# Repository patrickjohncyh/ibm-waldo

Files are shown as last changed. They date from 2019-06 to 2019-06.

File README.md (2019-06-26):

WALDO
======

Introduction
------------

People with learning disabilities can encounter difficulty in expressing themselves in speech. Makaton is a language programme that uses signs and symbols to enable users of all ages to communicate effectively. WALDO is a machine learning-enabled assisted living device meant for use by Makaton users and their carers in a care home setting. WALDO’s capabilities include:

* Makaton sign language interpretation using machine learning
* Easy-to-use interface, and a cute and endearing package to encourage use by people with learning disabilities and their carers
* Programmable buttons for users to quickly express pre-set phrases or emotions

Intended Use
---

WALDO is intended for use in a care home setting in the following ways:

Makaton sign interpretation
1. Makaton user (care home patient) signs to WALDO
2. WALDO uses machine learning to interpret sign
3. WALDO vocalises sign for carer to understand what user intends to express
4. Carer reacts accordingly, completing the interaction between the user and carer
This implementation enables the carer to understand the user without having to undergo the time-consuming process of learning Makaton.

Expression of pre-set phrases/emotions
1. User (by him/herself, or via carer) sets common phrases that he/she uses frequently to correspond to physical buttons on WALDO
2. User labels buttons accordingly for ease of use
3. User presses the relevant button, WALDO vocalises pre-set phrase
4. Carer responds accordingly
This implementation enables people with learning disabilities that have difficulty expressing themselves in speech to easily express everyday sentiments.

Virtual Design History File Overview
---

This is an overview of the various sections and subsections of WALDO's Virtual Design History File (VDHF). The VDHF details the developmental process of WALDO, the necessary steps to recreate it and the ethical and sustainability considerations of WALDO.

<table>
  <tr>
    <th width="18%">Section</th>
    <th width="22%">Subsection</th>
    <th>Description</th>
  </tr>
  <tr>
    <td colspan="2"><span style="font-weight:bold">Overview</span></td>
    <td>Overview of WALDO, contents of Virtual Design History File</td>
  </tr>
  <tr>
    <td rowspan="3"><span style="font-weight:bold">1. Setup</span></td>
    <td> <a href="https://github.com/patrickjohncyh/ibm-waldo/blob/master/1-Setup/1-1-Jetson-Setup.md">1.1 Jetson Nano Setup</a></td>
    <td>Jetson Nano Setup Guide</td>
  </tr>
  <tr>
    <td><a href="https://github.com/patrickjohncyh/ibm-waldo/blob/master/1-Setup/1-2-Pi-Setup.md">1.2 Pi Setup</a></td>
    <td>Raspberry Pi Setup Guide</td>
  </tr>
  <tr>
    <td><a href="https://github.com/patrickjohncyh/ibm-waldo/blob/master/1-Setup/1-3-Hardware-Connections.md">1.3 Hardware Setup</a></td>
    <td>Diagram of device hardware connections</td>
  </tr>
  <tr>
    <td rowspan="5"><span style="font-weight:bold">2. Machine Learning</span></td>
    <td><a href="https://github.com/patrickjohncyh/ibm-waldo/blob/master/2-MachineLearning/2-1-Machine-Learning.md"> 2.1 Machine Learning </a></td>
    <td>Details model design history and evolution as well as implementation on the edge device</td>
  </tr>
  <tr>
    <td><a href="https://github.com/patrickjohncyh/ibm-waldo/blob/master/2-MachineLearning/2-2-Server-Environment-Setup.md"> 2.2 Server Environment Setup</a></td>
    <td>Setting up server environment for further model training</td>
  </tr>
  <tr>
    <td><a href="https://github.com/patrickjohncyh/ibm-waldo/tree/master/2-MachineLearning/server-training"> Server Training Code</a></td>
    <td>Code to be run on server for model training</td>
  </tr>
  <tr>
    <td><a href ="https://github.com/patrickjohncyh/ibm-waldo/tree/master/2-MachineLearning/jetson-execution">Jetson Nano Execution Code</a></td>
    <td>Code to be run on Jetson Nano for Makaton sign recognition</td>
  </tr>
  <tr>
    <td><a href = "https://github.com/patrickjohncyh/ibm-waldo/tree/master/2-MachineLearning/jetson-execution/checkpoint_models"> Model and Weights</a></td>
    <td>Saved weights of the final trained model</td>
  </tr>

  <tr>
    <td rowspan="4"><span style="font-weight:bold">3. Raspberry Pi</span></td>
    <td><a href="https://github.com/patrickjohncyh/ibm-waldo/blob/master/3-Pi/3-1-Pi-Function.md"> 3.1 Overview of Pi Function</a></td>
    <td>Outline of functions and connections of Pi</td>
  </tr>
  <tr>
    <td><a href="https://github.com/patrickjohncyh/ibm-waldo/tree/master/3-Pi/pi-execution"> Pi Execution Code</td>
    <td>Code to be run on Raspberry Pi for high level tasks and audio generations through the IBM Watson text to speech module</span></td>
  </tr>
  <tr>
    
  </tr>
  <tr>
    
  </tr>
  <tr>
    <td rowspan="3"><span style="font-weight:bold">4. Hardware</span></td>
    <td><a href="https://github.com/patrickjohncyh/ibm-waldo/tree/master/4-Hardware/4-1-3D-Printing-STL-Files">4.1 3D printing files</a></td>
    <td>Contains Standard Tessellation Language (STL) files of the Jetson Nano case, the Pi case, the button support structure and WALDO’s eyepiece</td>
  </tr>
  <tr>
    <td><a href="https://github.com/patrickjohncyh/ibm-waldo/blob/master/4-Hardware/4-2-Power-Supply.md">4.2 Power Supply</td>
    <td>Summary of considerations when choosing WALDO’s power supply</td>
  </tr>
  <tr>
    <td><a href="https://github.com/patrickjohncyh/ibm-waldo/blob/master/4-Hardware/4-3-Hardware-List.md">4.3 Hardware List</td>
    <td>List of all hardware components used in assembly of WALDO</td>
  </tr>
  <tr>
    <td rowspan="4"><span style="font-weight:bold">5. Administrative</span></td>
    <td><a href="https://github.com/patrickjohncyh/ibm-waldo/tree/master/5-Administrative/5-1-Record-of-Meetings">5.1 Record of Meetings</td>
    <td>Meeting minutes and decisions made</td>
  </tr>
  <tr>
    <td><a href="https://github.com/patrickjohncyh/ibm-waldo/blob/master/5-Administrative/5-2-Gantt-Chart.md">5.2 Gantt Chart</td>
    <td>Intended timeline of project (plotted during first meeting at IBM Hursley)</td>
  </tr>
  <tr>
    <td><a href="https://github.com/patrickjohncyh/ibm-waldo/blob/master/5-Administrative/5-3-Bill-of-Materials.md">5.3 Bill of Materials</td>
    <td>Record of expenditure and outline of cost of device</td>
  </tr>
  <tr>
    <td><a href="https://github.com/patrickjohncyh/ibm-waldo/blob/master/5-Administrative/5-4-Data-Collection.md">5.4 Data Collection</td>
    <td>Outline of procedure, considerations and product of data collection</td>
  </tr>
  <tr>
    <td rowspan="6"><span style="font-weight:bold">6. Miscellaneous</span></td>
    <td><a href="https://github.com/patrickjohncyh/ibm-waldo/blob/master/6-Miscellaneous/6-1-Ethical-Considerations.md">6.1 Ethical Considerations</td>
    <td>Outline of ethical considerations in the design, building and use of WALDO</td>
  </tr>
  <tr>
    <td><a href="https://github.com/patrickjohncyh/ibm-waldo/blob/master/6-Miscellaneous/6-2-Sustainability-Considerations.md"> 6.2 Sustainability considerations</td>
    <td>Outline of sustainability considerations in the design, building and use of WALDO</td>
  </tr>
  <tr>
    <td><a href="https://github.com/patrickjohncyh/ibm-waldo/blob/master/6-Miscellaneous/6-3-Blog.md">6.3 Blog</td>
    <td>Rationale behind the blog and links to the blog posts</td>
  </tr>
  <tr>
    <td><a href="https://github.com/patrickjohncyh/ibm-waldo/blob/master/6-Miscellaneous/6-4-Future-Work.md">6.4 Future Work</td>
    <td>Discussion of present implementation and possible extensions to the project</td>
  </tr>
  <tr>
    <td><a href="https://github.com/patrickjohncyh/ibm-waldo/blob/master/6-Miscellaneous/6-5-Leaflet.pdf">6.5 Leaflet</td>
    <td>Informational leaflet on WALDO</td>
  </tr>
  <tr>
    <td><a href="https://github.com/patrickjohncyh/ibm-waldo/blob/master/6-Miscellaneous/6-6-Poster.pdf">6.6 Poster</td>
    <td>Poster for hackbooth and presentation</td>
  </tr>
</table>

Acknowledgements
---

The WALDO team consists of 5 students from the Electrical Engineering (EE) Department of Imperial College London. The key tasks performed by each member is as follows,

1. [Joshua Chan](https://github.com/josh8chan) : Administrative, Data Collection, Peripheral Sensors Implementation 
2. [Lua Ying Hao](https://github.com/Kaynelua) : Jetson Nano Implementation, Machine Learning
3. [Ng Yi Song](https://github.com/NgYiSong) : Data Collection, Peripheral Sensors Implementation
4. [Patrick John Chia](https://github.com/patrickjohncyh) : Jetson Nano Implementation, Machine Learning
5. [Yeow En Kai Joel](https://github.com/joelyeow) : Administrative, Data Collection and Processing, Peripheral Sensors Implementation 

We would like to thank:

1. Dr Steve Wright, for his invaluable guidance and encouragement throughout the project
2. Louise Cooper, John McNamara & Emily Larkin from IBM for their clear direction and unwavering support in the implementation of this project
3. Precious Homes, for supporting this project by providing valuable insight into the use of Makaton, as well as training videos
4. Vic, May & Amine at the teaching labs, for their untiring technical support
5. All who volunteered their time to help us in the collection of training data

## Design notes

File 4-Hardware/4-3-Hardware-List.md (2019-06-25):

# 4.3 List of Main Hardware Components

The following table shows the various components bought and used in the assembly of WALDO:

<Br>

| Item                                 	| Product Description                                                                                                                                                                  	| Manufacturer    	| Quantity 	| 
|--------------------------------------	|--------------------------------------------------------------------------------------------------------------------------------------------------------------------------------------	|-----------------	|----------	|
| Elephant Stuffed Toy                 	| Fuddlewuddle Elephant, Medium- H23 cm                                                                                                                                                	| Jellycat        	| 1        	| 
| Jetson Nano                          	| NVIDIA Jetson Nano Developer Kit                                                                                                                                                     	| NVIDIA          	| 1        	| 
| 64GB Micro SD Card for Jetson        	| INMSDX64G10-90U1 - 64GB Ultima Pro Class 10 MicroSDXC Memory Card with SD Adaptor 90MB/s                                                                                             	| Integral        	| 1        	| 
| Cooling Fan for Jetson               	| Noctua NF-A4x20 5V PWM, Premium Quiet Fan, 4-Pin, 5V Version (40x20mm, Brown)                                                                                                        	| Noctua          	| 1        	| 
| Power Adapter for Jetson             	| RS PRO, 20W Plug In,Power Supply 5V, 4A, Level VI Efficiency, 1 Output Switched Mode Power Supply, 3-Pin UK                                                                          	| RS PRO          	| 1        	| 
| Webcam                               	| Logitech C920 HD Pro Webcam                                                                                                                                                          	| Logitech        	| 1        	|
| Wifi Dongle                          	| EW-7811UN - N150 Wi-Fi Nano USB Adaptor                                                                                                                                              	| Edimax          	| 1        	| 
| Power Bank                           	| Krisdonia Laptop Power Bank 25000mAh Portable Charger with Type-C Port + DC Port + Dual USB (QC3.0 Quick Charge) for Laptop, Tablet, Cell phone, Macbook, Camera, Projector and more 	| Krisdonia       	| 1        	| 
| Raspberry Pi                         	| Raspberry Pi 3 Model B                                                                                                                                                               	| Raspberry Pi    	| 1        	| 
| 8GB Micro SD Card for Raspberry Pi   	| Kingston 8GB Micro SDHC Class 4 Memory Card                                                                                                                                          	| Kingston        	| 1        	| 
| Speakers                             	| 00173130 - Sonic Mobil 181 2.0 PC Speakers 3W Black                                                                                                                                  	| Hama            	| 1        	|
| Buttons                              	| 1825910-6: Black Button Tactile Switch, Single Pole Single Throw (SPST) 50 mA @ 24 V dc 1.4mm                                                                                        	| TE Connectivity 	| 4        	| 
| Ultrasonic sensor                    	| Parallax Inc 28015, PING))) Ultrasonic Distance Sensor Module                                                                                                                        	| Parallax Inc    	| 1        	| 
| Hook and Loop Fasteners- Velcro Tape 	| VELCRO Brand Stick On For,Fabrics Tape, 19 mm x 60 cm - White                                                                                                                        	| Velcro Brand    	| 1        	| 

<Br>

> Note that some of the supplementary and commonly found hardware such as jumper cables, wires and the 3D Prints were not included in this list.

<Br>
  
> Also note that this list does not show the cost of each item. The Bill of Materials (which shows the cost of each item) can be found by navigating to "5-Adminisitrative > [5-3-Bill-of-Materials.md](https://github.com/patrickjohncyh/ibm-waldo/blob/master/5-Administrative/5-3-Bill-of-Materials.md)".

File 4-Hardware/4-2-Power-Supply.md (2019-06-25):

# 4.2 Power Source

A strong and stable power supply is needed to power WALDO. In order to choose an appropriate power supply, the power consumption of the individual components of WALDO first needs to be known. This is summarised in the table below. 

| Component                 	| Typical Current Drawn / A 	| Power       Consumption / W 	|
|---------------------------	|:-------------------------:	|:---------------------:	|
| Jetson Nano Developer Kit 	|         1.0 - 2.0         	|       5.0 - 10.0      	|
| Raspberry Pi              	|            0.7            	|          3.5          	|
| Speakers                  	|            0.6            	|          3.0          	|

As such, the power source has to be able to supply about 20W of power to ensure stable and smooth operation. The biggest source of power consumption comes from the Jetson Nano when it is performing its Machine Learning inference task. The most efficient way to power the Jetson Nano would be through the DC barrel jack connector. However, in order to do so, a jumper pin needs to be placed on J48 on the Jetson board, as seen in the diagram below. This enables the Jetson to be powered through the barrel jack.

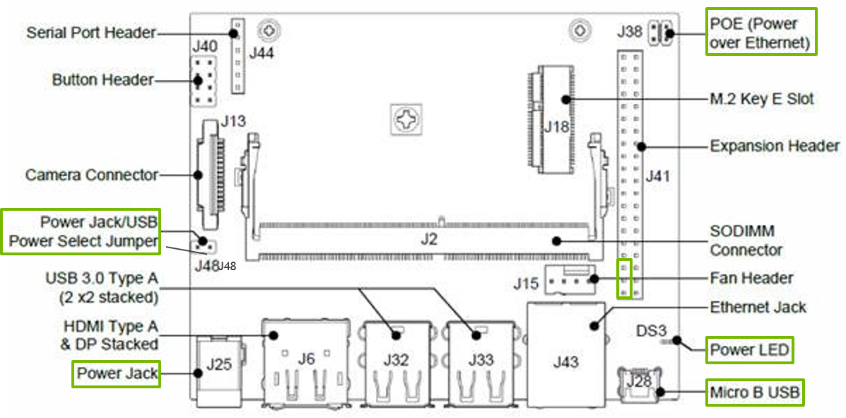
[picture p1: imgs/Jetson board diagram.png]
Jetson Board Layout


One way to power the Jetson would be to use a 4A, 5V plug-in power adapter from the mains. However, this means that WALDO would no longer be portable hence making this option not ideal.

As such, a large power bank was used instead. As a rule of thumb, the power bank chosen should be one capable of charging laptops and should have a DC output port. In this project, the Krisdonia Laptop Power Bank 25000mAh Portable Charger was used. This power bank has a DC output port and 2 USB ports, which fits in nicely for the number of components that require power. The Jetson Nano is connected through the DC output port, while the Raspberry Pi and speakers are connected through the 2 USB ports. The Raspberry Pi uses a USB to micro USB connection for power, as seen from the hardware connections diagram below.

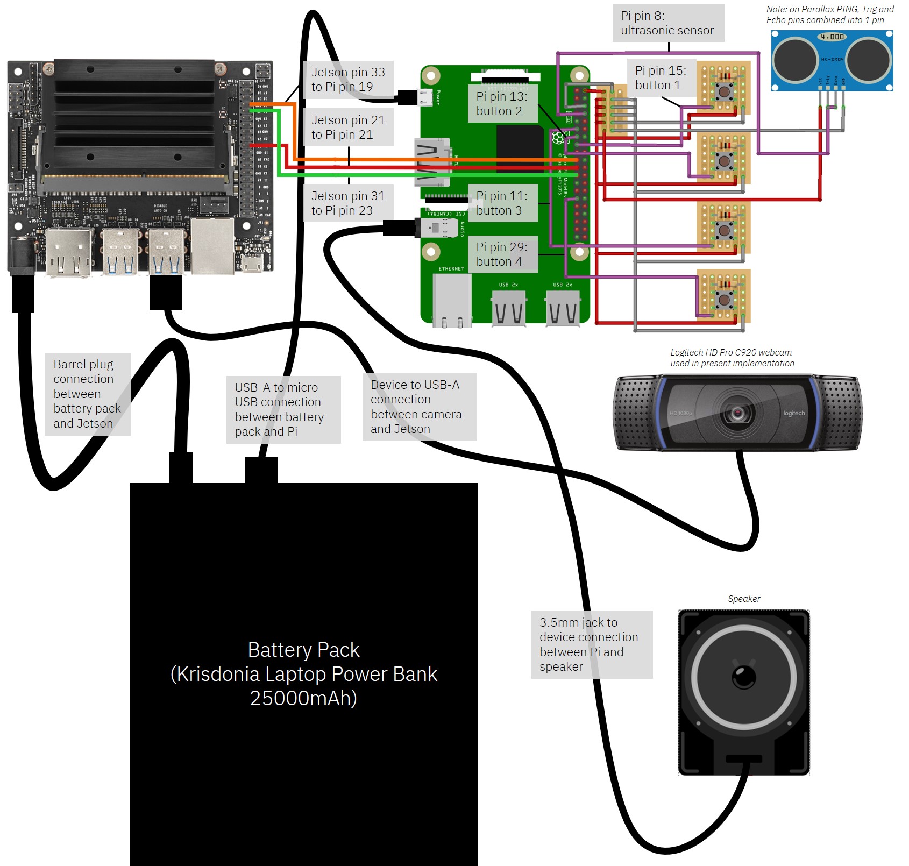
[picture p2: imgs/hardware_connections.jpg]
Hardware Connections

  
A power bank was utilised as an “off the shelf” solution for this prototype not only due to time limitations, but also because it is deemed to be safer and more reliable, having passed industry safety checks. The downside is that this power bank is rather costly at a retail price of £98. In the future, rechargeable lithium ion batteries coupled with some applications of power electronics could be used instead as a more cost-effective alternative.

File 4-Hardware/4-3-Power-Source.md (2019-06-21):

# Power Source

A strong and stable power supply is needed to power WALDO. In order to choose an appropriate power supply, the power consumption of the individual components of WALDO first needs to be known. This is summarised in the table below. 

| Component                 	| Typical Current Drawn / A 	| Power       Consumption / W 	|
|---------------------------	|:-------------------------:	|:---------------------:	|
| Jetson Nano Developer Kit 	|         1.0 - 2.0         	|       5.0 - 10.0      	|
| Raspberry Pi              	|            0.7            	|          3.5          	|
| Speakers                  	|            0.6            	|          3.0          	|

<Br>

As such, the power source has to be able to supply about 20W of power to ensure stable and smooth operation. The biggest source of power consumption comes from the Jetson Nano. The most efficient way to power the Jetson Nano would be through the DC barrel jack connector. However, in order to do so, a jumper pin needs to be placed on J48 on the Jetson board, as seen in the diagram below. This enables the Jetson to be powered through the barrel jack.

<Br>
  
Jetson Board Layout

<Br>

One way to power the Jetson would be to use a 4A, 5V plug-in power adapter from the mains. However, this means that WALDO would no longer be portable hence making this option not ideal.

As such, a large power bank was used instead. As a rule of thumb, the power bank chosen should be one capable of charging laptops and should have a DC output port. In this project, the Krisdonia Laptop Power Bank 25000mAh Portable Charger was used. This power bank has a DC output port and 2 USB ports, which fits in nicely for the number of components that require power. The Jetson Nano is connected through the DC output port, while the Raspberry Pi and speakers are connected through the 2 USB ports. The Raspberry Pi uses a USB to micro USB connection for power, as seen from the hardware connections diagram below.

<Br>

Hardware Connections
  
<Br>

A power bank was utilised as an “off the shelf” solution for this prototype not only due to time limitations, but also because it is deemed to be safer and more reliable, having passed industry safety checks. The downside is that this power bank is rather costly at a retail price of £98. In the future, perhaps rechargeable lithium ion batteries coupled with some applications of power electronics could be used instead as a more cost-effective alternative.

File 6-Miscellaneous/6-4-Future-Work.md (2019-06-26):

# 6.4 Future Work
This section is a discussion of the present implementation and possible extensions to the project.

## Go To
* 6.4.1 [Discussion of Present Implementation](#641-discussion-of-present-implementation)
* 6.4.2 [Improvements to Present Hardware](#642-improvements-to-present-hardware)
* 6.4.3 [Addidtional Capabilities](#643-additional-capabilities)

## 6.4.1 Discussion of Present Implementation

The table below shows the capabilities of WALDO that have and have not been implemented.

| No. 	| Capability                                                        	| Status                                                                                                                              	|
|-----	|-------------------------------------------------------------------	|-------------------------------------------------------------------------------------------------------------------------------------	|
| 1.  	| Makaton interpretation using machine learning                     	| **Implemented** - Interpretation of 5 signs with high accuracy and low latency.<br> **Not Implemented** - Interpretation of other Makaton signs 	|
| 2.  	| Buttons to output pre-set expressions                             	| **Implemented**                                                                                                                         	|
| 3.  	| User interface to change what expressions button presses output   	| **Not Implemented** - Strings that buttons output cannot be changed remotely, no user interface to change string output                 	|
| 4.  	| Ambient sensors to analyse and understand the user’s surroundings 	| **Not Implemented** - Potential to add additional sensors given free GPIO pins on Pi                                                                                                                   	|
| 5.  	| Replicability of product                                          	| **Implemented** - easy transition to mass produce product at lower cost                                                	|

## 6.4.2 Improvements to Present Hardware

Presently, WALDO faces several challenges arising from the limited capabilities its hardware components can offer, namely:

-   The Nvidia Jetson Nano used for Makaton interpretation is a developer kit meant for rapid prototyping, and has insufficient RAM to run a larger and more complex model
    
-   The battery pack used, a Krisdonia 25000mAh battery pack, is unable to handle power surges from the Jetson when at its full computing potential, causing the battery pack to shut off power as a safety mechanism. Hence, the Jetson is run with only 3 out of its 4 cores, and at a clock speed lower than its maximum operating frequency
    
-   Several functions of WALDO have been offloaded to a Raspberry Pi to relieve computational load on the Jetson. This increases the amount of physical electronic hardware that has to be placed in the toy

Using purpose-built electronic components in WALDO, with higher GPU RAM and more CPU cores or higher clock speeds, would obviate the need for two embedded devices to be present, reducing the physical space needed within the toy for electronic hardware and reducing the chance of failure of one of the components. In addition, using an appropriate battery, instead of a battery pack with a built-in safety mechanism, would allow computation to be performed at the embedded device’s full potential. A safety mechanism with a higher threshold could be used with the battery to ensure safety is not compromised.

The external physical components of WALDO could also stand to be improved. Improvements include sewing the electronic hardware onto the cotton of the device to improve robustness against rough handling, including a zip to allow easy access to WALDO’s interior devices, sewing holes into WALDO’s exterior to allow for convenient access to ports, and adding a physical on-off switch or a camera shutter for privacy.

## 6.4.3 Additional Capabilities

The first, and most apparent, area in which WALDO could stand to be improved is in increasing the number of signs it can recognise. However, this is a time-consuming process due to the lack of an online Makaton database with which to train the machine learning model. As such, the following changes could be made to the data collection process if the number of signs to be recognised is to be drastically increased.

-   Use an institutionally-supported mechanism to collect training data. One method would be to offer volunteers a small amount of cash each, while keeping it within an educational institution. Another method would be to outsource data collection to a third party, such as through the use of Amazon’s Mechanical Turk[1], an online outsourcing platform where volunteers are paid for their effort.
    
-   Using machine learning or pattern recognition to automatically preprocess videos for training. This process was hugely time-consuming when performed manually.
    
-   Sourcing data from around the world, instead of only within the UK, to improve robustness of sign recognition

Another capability that could be integrated into WALDO’s Makaton interpretation is the ability to learn on-the-go. Presently, WALDO uses a pre-trained model and does not retain user data for additional training. If WALDO is used by an individual user for an extended period of time, on-the-go learning could be implemented to enable predictions to improve over time.

However, implementing such a feature on WALDO faces several problems, which are not insurmountable. Firstly, there would have to be a mechanism by which the user labels the signs he is performing. This could be done through a feedback system, whereby the user provides positive or negative feedback to WALDO based on whether the prediction is correct. This feedback mechanism would in turn have to be implemented. Secondly, on-the-go learning raises a privacy concern as the user’s data would have to be stored, and may have to be uploaded to a remote server if WALDO does not have sufficient computing power to train the machine learning model. This could be addressed by clearer privacy guidelines on WALDO’s use and strict encryption protocols.

A user interface to change the expressions WALDO outputs when its buttons are pressed has not been implemented. Since both the Pi and the Jetson have Internet connectivity, implementing this function should be straightforward; the interface could either be a webpage or a phone app. The user (or carer) would change the expression to be output, which would in turn change the string passed into the IBM Watson text-to-speech software.

Ambient sensors to analyse and understand the user’s environment have yet to be implemented. These sensors could be integrated with the Pi, sending information via the GPIO pins or tailor-made breakout boards and stored on the Pi for later analysis by medical professionals. Understanding the environment and possible risk factors is important in caring for people with learning disabilities[2], hence sensors that could be implemented include ambient light, sound and temperature sensors.

## Bibliography

[1] Amazon. Overview. *Amazon Mechanical Turk.* [Online] Available from: https://www.mturk.com/ [Accessed: 18 June 2019].

[2] National Institute for Health and Care Excellence. (2015) NG11. *Challenging behaviour and learning disabilities: prevention and interventions for people with learning disabilities whose behaviour challenges.* NICE.

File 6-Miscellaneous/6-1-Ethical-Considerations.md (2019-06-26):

# 6.1 Ethical Considerations

As a device meant for use with vulnerable people and relying on a significant amount of data collection, WALDO raises several ethical concerns that need to be addressed. In this report, this group will examine whether these concerns are founded, and outline what steps have been taken in this project to address them.
  
## Go To 
* 6.1.1 [User Privacy](#611-user-privacy)
* 6.1.2 [Data Privacy](#612-data-privacy)
* 6.1.3 [Consequnces for Jobs](#613-consequences-for-jobs)
  
## 6.1.1 User Privacy

In recent years, with advancements in connectivity and sensor technology, smart home devices have become increasingly ubiquitous in developed countries[1][2]. However, data privacy is one key concern for smart home users; concerns include[3]:

-   Who has access to smart home data: manufacturers are more trusted than government entities, which are in turn more trusted than ISPs
    
-   What data the smart home device is recording: devices that do not record audio and video are more likely to be trusted
    
-   What privacy protections manufacturers have in place

While WALDO is not strictly a smart home device, it possesses many characteristics similar to that of a smart home device:

-   WALDO includes a camera and environmental sensors which are always on
    
-   WALDO is meant for use in a care home setting, which is similar to a home setting as it is a form of long-term habitation for patients
    
-   WALDO can be connected to the Internet

As such, the privacy concerns that face smart home technologies would face WALDO too, and have to be addressed. Arguably, these concerns are all the more pressing, since WALDO is meant for use with people with learning disabilities, who are more vulnerable than everyday consumers. For example, they might be less aware of the reality of privacy breaches and hacking, and more willing to use a device that is not safe for use. While it may be argued that the onus is on the care home to ensure their residents’ privacy, and care homes such as Precious Homes(1) have their own privacy policy[4], this group believes that WALDO should be built with its users’ privacy as one of its foremost considerations.

> (1) Precious Homes is the care home that this group worked with during this project, and provided recommendations on the use of Makaton

The first way in which WALDO addresses privacy concerns is in being an on-edge device, with the on-device Nvidia Jetson Nano having sufficient computational power to perform machine learning computation on its own. This obviates the need to send user data, that is, the video used for Makaton interpretation, to a remote server, where it could be compromised or misused.

The second way in which WALDO addresses privacy concerns is in not recording more data than it needs to. Besides the camera, WALDO does not contain a microphone, and cannot record conversations around it. Environmental sensors, should they be implemented, do not provide data that can be linked to specific individuals, and would only be used to detect trends in the user’s environment.

Additional steps to address privacy concerns could include a physical shutter over the camera for when WALDO is not in use, and physical airgapping between network-connected devices and recording devices when Internet connectivity is not required. However, Internet connectivity should still be retained, to allow for software updates to be provided to WALDO, for example, to improve the accuracy and robustness of its machine learning model.

## 6.1.2 Data Privacy

In making use of machine learning to perform Makaton interpretation, WALDO requires the collection of a large amount of training data from volunteers. This raises the concern of data privacy of the volunteers, as training data has the potential to be misused. This group has addressed this concern by destroying training data after training has been completed, only providing IBM with the trained model. Further elaboration on this point can be found in the ‘Data Collection’ document under ‘5. Administrative > Data Collection’.

## 6.1.3 Consequences for Jobs

A concern with any technological device meant to perform a role previously carried out by a person is the impact on the jobs and livelihoods of workers in that industry. As a Makaton interpreter and companion, WALDO performs several roles that care home carers currently performs. However, WALDO is meant to augment the capabilities of carers, not replace them. WALDO only performs Makaton interpretation, but is unable to act on the signs it interprets, relying on carers to carry out that role. Hence, WALDO is meant to ease interaction between carer and resident, not replace the carer. As WALDO is only a medium for expression, it is unable to act as a true companion that responds, thus also does not supplant the carer in this aspect.

In conclusion, WALDO has been designed and built specifically with the above mentioned ethical considerations in mind, with specific measures to safeguard privacy and work within existing care home structures. In addition, these considerations should remain a priority when planning further extensions to WALDO.

## Bibliography

[1] Snow, A. *Americans Ready for the Smart Home*. [Online] Coldwell Banker Blue Matter. Available from: https://www.coldwellbanker.com/blog/americans-ready-for-the-smart-home/?utm_source=pr&utm_medium=referral&utm_campaign=pr-blog-smarthomes&utm_content=CNET [Accessed: 18 June 2019].

[2] Alton, L. Are Customers Finally Ready to Adopt Smart Home Technology? *Huffington Post*. [Online] 2017; Available from: https://www.huffpost.com/entry/are-customers-finally-ready-to-adopt-smart-home-technology_b_59e6e735e4b0e60c4aa3666f [Accessed: 18 June 2019].

[3] Zheng, S., Apthorpe, N., Chetty, M. & Feamster, N. (2018) User Perceptions of Smart Home IoT Privacy. *Proceedings of the ACM on Human-Computer Interaction - CSCW*. [Online] 2 (CSCW). Available from: doi:10.1145/3274469 [Accessed: 18 June 2019].

[4] Gennings, W. (n.d.) *Privacy Notice*. [Online]. Precious Homes. Available from: http://www.precious-homes.co.uk/privacy-policy/ [Accessed: 18 June 2019].

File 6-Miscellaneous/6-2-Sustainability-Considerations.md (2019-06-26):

#  6.2 Sustainability Considerations

Go To
------
* 6.2.1 [Environmental Sustainbility](#621-environmental-sustainability)
* 6.2.2 [Economic Sustainability](#622-economic-sustainability)

## 6.2.1 Environmental Sustainability

Electronic waste is a growing environmental concern around the world[1], as devices are increasingly built with shorter product cycles. In this regard, as a device with many electronic components, WALDO could potentially contribute to this problem.

WALDO is intended for use in care homes by residents with learning disabilities and their carers. With its relatively fixed capabilities, and since updates to the product would primarily be delivered via software updates to the machine learning model used, WALDO should have a long product lifespan. Furthermore, a long lifespan would enable WALDO to better fulfil the role of being a companion, as the care home resident gets more used to its presence and interacting with it.

In spite of this, this group believes that sustainability should still be a consideration when designing a replicable production version of WALDO. Several measures that can be taken to reduce WALDO’s environmental impact include:

-   Using a soft toy that is environmentally friendly as the device exterior. Environmentally friendly soft toys can be built with recycled materials or be built to be recyclable, and make use of non-toxic or organic materials in their construction[2]
    
-   Reducing the number of electronic components used. One method of doing this would be to use a custom-built integrated circuit that is able to handle all the computation required, instead of two embedded devices (Jetson and Pi) in the current implementation
    
-   Providing disposal information with the WALDO device, to ensure that WALDO is disposed of in a responsible manner, and relevant components are recycled

## 6.2.2 Economic Sustainability

A study in 2014 led by the London School of Economics and Political Science (LSE) estimates that autism costs the UK at least £32 billion per year in treatment and lost earnings and is the country’s number one most costly[3] medical condition. The adult specialist care market, which is WALDO’s target market, was valued at nearly £16 billion in 2017[4], a share that is forecast to increase. Care for people with learning disabilities takes up approximately half this amount[5].

In addition, a study done by the Personal Social Service Research Unit (PSSRU) and University of Kent in 2018 shows that recruiting and training staff in autism and learning disability supported care homes cost the homes an average of about £1,012[6] per client per year.

With WALDO possibly being a one time fixed cost(<£400) with low maintenance fees, employing the use of WALDO in care homes will certainly provide care homes with cost savings of about £1,000 per client per year. The cost savings can also be transferred to patients, thus reducing the cost of care for residents with additional needs. Cost savings can also be realised for patients not residing in care homes but in their own residential homes. As such, WALDO could certainly bring economic benefits to all stakeholders involved and is an economically sustainable solution.

## Bibliography

[1] Semuels, A. (23 May 2019) The World Has an E-Waste Problem. *Time*. [Online] Available from: https://time.com/5594380/world-electronic-waste-problem/ [Accessed: 18 June 2019].

[2] Skye, J. (n.d.) *Earth Friendly Toys*. [Online]. LoveToKnow. Available from: https://greenliving.lovetoknow.com/Earth_Friendly_Toys [Accessed: 18 June 2019].

[3] Anonymous. (10 June 2014) Autism is the most costly medical condition in the UK. *London School of Economics and Political Science (LSE)*. [Online]. Available from: http://www.lse.ac.uk/website-archive/newsAndMedia/newsArchives/2014/06/Autism.aspx [Accessed : 19 June 2019].

[4] Anon (2017) Care homes market study: Final report. 

[5] Laing, W. (2016) *Complex care market looking ‘broadly positive’: Headline findings from LaingBuisson’s latest research and analysis.* LaingBuisson Healthcare Intelligence. Available from: https://www.laingbuisson.com/wp-content/uploads/2018/02/LaingBuisson_Adult_Specialist_Care_2ed_market_briefing.pdf [Accessed: 19 June 2019].

[6] Curtis, Lesley A. and Burns, Amanda (2018) Unit Costs of Health and Social Care 2018. *University of Kent.* [Online] Available from: https://doi.org/10.22024/UniKent/01.02.70995 [Accessed : 19 June 2019].

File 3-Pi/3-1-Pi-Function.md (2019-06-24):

3.1 Overview of Pi Function
=======================

To relieve the computational load imposed on the Jetson, all functions other than running the machine learning model have been offloaded to a Raspberry Pi 3 Model B. This allows the Jetson to be used to identify Makaton signs with low latency and high inference rate. The functions the Pi performs are:

* Send audio files to speaker to provide device’s speech output
* Receive information from device buttons, output user-customised responses
* Receive information from proximity sensor
* Receive information from Jetson Nano regarding state of readiness and Makaton sign identified

Hence, the Pi runs the high level logic of the device, bringing together information from the sensors, buttons and Jetson, after which it determines the appropriate output and plays it on the connected speaker.

<Br>
  
Proximity Sensor
---------------

The proximity sensor used is the Parallax PING Ultrasonic Sensor. The sensor works as follows: the I/O pin triggers an ultrasonic burst, after which it measures the time required for an echo to be received. In WALDO, the proximity sensor is used to give the user a gauge of an appropriate distance for the user to be at to use its different functions.

The diagram below shows the functions corresponding to the different ranges between WALDO and the user.

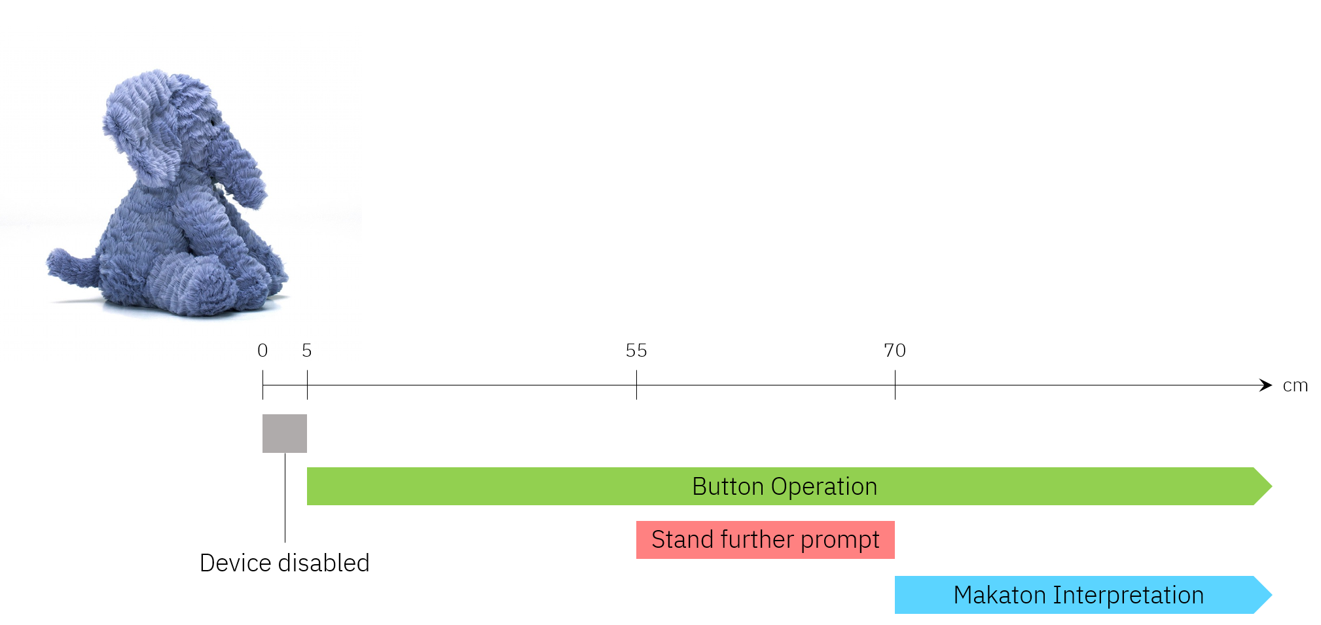
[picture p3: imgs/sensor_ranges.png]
Sensor Ranges


<Br>
  
The device is disabled if the proximity sensor is blocked, since it detects a range of less than 5cm. Between 5 and 55cm, the user can use the buttons. Between 55 and 70cm, WALDO interprets the user’s intention to be to perform Makaton interpretation, and directs them to stand further away to ensure that the user’s sign can be properly captured by the camera. If the user is further than 70cm away, Makaton interpretation is carried out and the relevant output is transmitted to the speaker.

<Br>
  
Function of Buttons
-------------------

WALDO has 4 hardware buttons. When one is pressed, the Pi detects the button press and plays the correct audio file using the connected speaker. This process is described by the flow diagram below.

<Br>

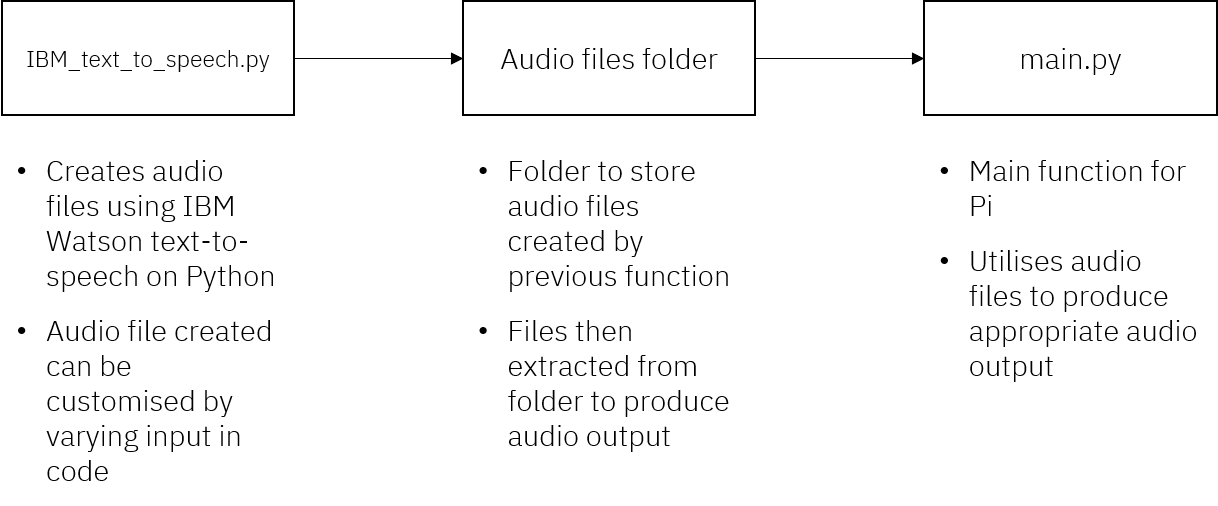
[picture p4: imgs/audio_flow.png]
Logic flow diagram for audio output from Pi


The IBM_text_to_speech.py code employs IBM Watson text-to-speech on Python to generate the audio files. The contents of the audio files can be edited to tailor the needs of the users by simply modifying or adding to the “predefined_actions” list in the code. The generated audio files are saved in a pre-determined folder on the Pi. In main.py, when a button is pressed, the relevant audio file is accessed and played via the speaker.

<Br>
  
Communication with Jetson
-------------------------

Makaton interpretation using machine learning has been implemented on the Jetson. As the output device, the speaker, is connected to the Pi, the Jetson needs to send the appropriate data to the Pi to produce the correct output. As only 7 messages are required in the present implementation, only 3 bits are necessary. Hence, the Jetson is connected to the Pi using 3 GPIO pins, as shown in the table below.

<Br>
  
|**Bit**|**Pin on Jetson**|**Pin on Pi**|
|-------|-----------------|-------------|
|Most significant|Pin 33 (GPIO38)|Pin 19 (GPIO10)|
|Middle|Pin 31 (GPIO200)|Pin23 (GPIO11)|
|Least significant|Pin 21 (GPIO17)|Pin21 (GPIO9)|

<Br>
  
When the Jetson has successfully booted up, a bit sequence of ‘111’ is transmitted to the Pi, producing an audio output of “I’m Ready”, letting the user know that the system is ready for use.

 <Br>

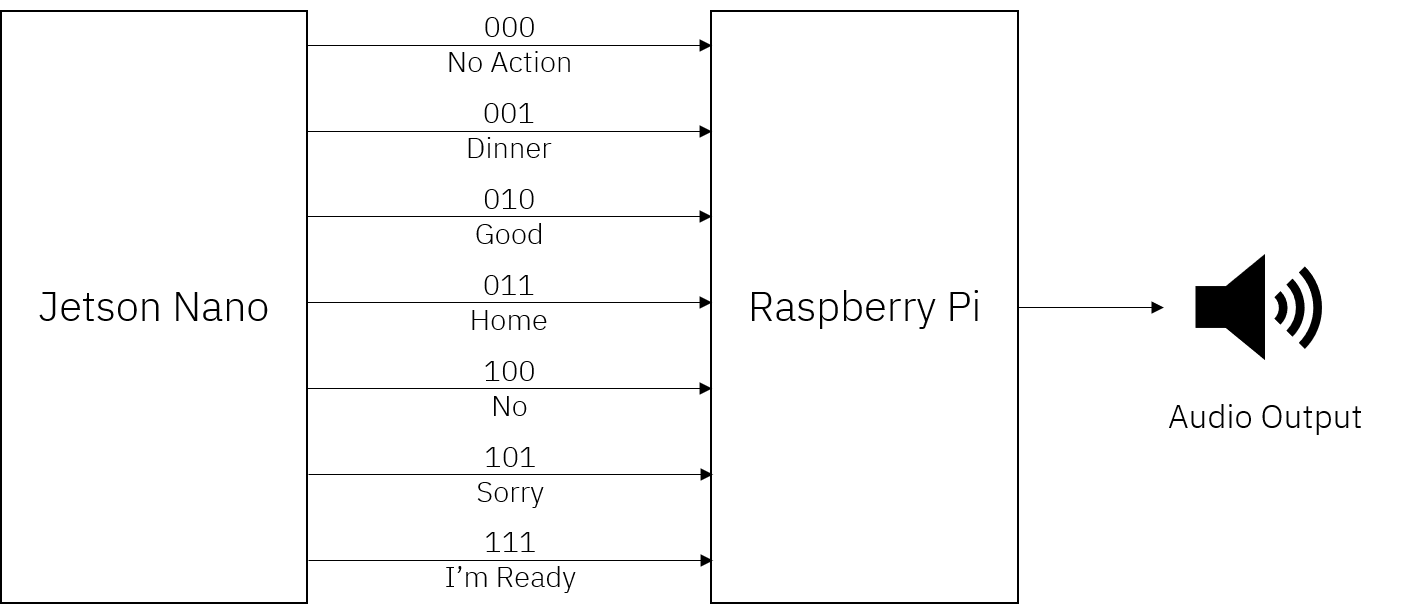
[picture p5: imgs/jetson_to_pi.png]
Pin connection between Jetson and Pi


<Br>

If the number of signs that can be interpreted increases, more GPIO pins can be used for communication.

<Br>

Overall Pi Function
-------------------

The logic flow diagram below describes the overall normal function of the Pi in WALDO.

<Br>

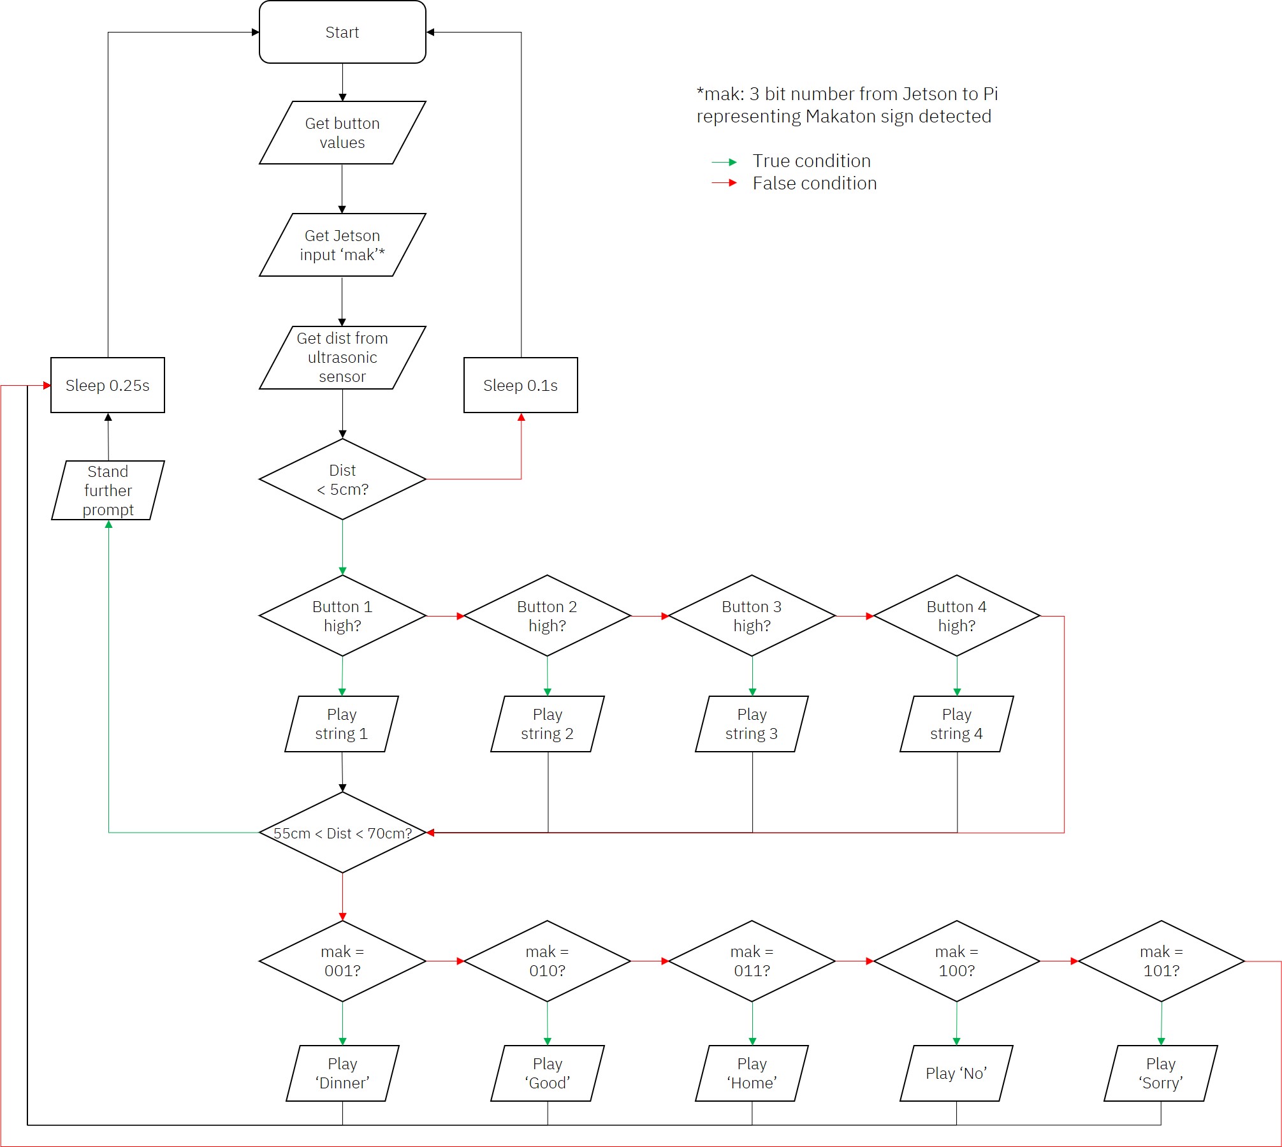
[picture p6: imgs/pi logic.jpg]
Pi logic flow diagram


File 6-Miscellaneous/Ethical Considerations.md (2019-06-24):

# Ethical Considerations

As a device meant for use with vulnerable people and relying on a significant amount of data collection, WALDO raises several ethical concerns that need to be addressed. In this report, this group will examine whether these concerns are founded, and outline what steps have been taken in this project to address them.
  
## Go To 
* [User Privacy](#user-privacy)
* [Data Privacy](#data-privacy)
* [Consequnces for Jobs](#consequences-for-jobs)
  
<Br>
  
## User Privacy

In recent years, with advancements in connectivity and sensor technology, smart home devices have become increasingly ubiquitous in developed countries[1][2]. However, data privacy is one key concern for smart home users; concerns include[3]:

-   Who has access to smart home data: manufacturers are more trusted than government entities, which are in turn more trusted than ISPs
    
-   What data the smart home device is recording: devices that do not record audio and video are more likely to be trusted
    
-   What privacy protections manufacturers have in place

<Br>  

While WALDO is not strictly a smart home device, it possesses many characteristics similar to that of a smart home device:

-   WALDO includes a camera and environmental sensors which are always on
    
-   WALDO is meant for use in a care home setting, which is similar to a home setting as it is a form of long-term habitation for patients
    
-   WALDO can be connected to the Internet
    
<Br>

As such, the privacy concerns that face smart home technologies would face WALDO too, and have to be addressed. Arguably, these concerns are all the more pressing, since WALDO is meant for use with people with learning disabilities, who are more vulnerable than everyday consumers. For example, they might be less aware of the reality of privacy breaches and hacking, and more willing to use a device that is not safe for use. While it may be argued that the onus is on the care home to ensure their residents’ privacy, and care homes such as Precious Homes(1) have their own privacy policy[4], this group believes that WALDO should be built with its users’ privacy as one of its foremost considerations.

> (1) Precious Homes is the care home that this group worked with during this project, and provided recommendations on the use of Makaton

<Br>
  
The first way in which WALDO addresses privacy concerns is in being an on-edge device, with the on-device Nvidia Jetson Nano having sufficient computational power to perform machine learning computation on its own. This obviates the need to send user data, that is, the video used for Makaton interpretation, to a remote server, where it could be compromised or misused.

The second way in which WALDO addresses privacy concerns is in not recording more data than it needs to. Besides the camera, WALDO does not contain a microphone, and cannot record conversations around it. Environmental sensors, should they be implemented, do not provide data that can be linked to specific individuals, and would only be used to detect trends in the user’s environment.

Additional steps to address privacy concerns could include a physical shutter over the camera for when WALDO is not in use, and physical airgapping between network-connected devices and recording devices when Internet connectivity is not required. However, Internet connectivity should still be retained, to allow for software updates to be provided to WALDO, for example, to improve the accuracy and robustness of its machine learning model.

<Br>

## Data Privacy

In making use of machine learning to perform Makaton interpretation, WALDO requires the collection of a large amount of training data from volunteers. This raises the concern of data privacy of the volunteers, as training data has the potential to be misused. This group has addressed this concern by destroying training data after training has been completed, only providing IBM with the trained model. Further elaboration on this point can be found in the ‘Data Collection’ document under ‘5. Administrative > Data Collection’.

<Br>

## Consequences for Jobs

A concern with any technological device meant to perform a role previously carried out by a person is the impact on the jobs and livelihoods of workers in that industry. As a Makaton interpreter and companion, WALDO performs several roles that care home carers currently performs. However, WALDO is meant to augment the capabilities of carers, not replace them. WALDO only performs Makaton interpretation, but is unable to act on the signs it interprets, relying on carers to carry out that role. Hence, WALDO is meant to ease interaction between carer and resident, not replace the carer. As WALDO is only a medium for expression, it is unable to act as a true companion that responds, thus also does not supplant the carer in this aspect.

In conclusion, WALDO has been designed and built specifically with the above mentioned ethical considerations in mind, with specific measures to safeguard privacy and work within existing care home structures. In addition, these considerations should remain a priority when planning further extensions to WALDO.

<Br>

## Bibliography

[1] Snow, A. *Americans Ready for the Smart Home*. [Online] Coldwell Banker Blue Matter. Available from: https://www.coldwellbanker.com/blog/americans-ready-for-the-smart-home/?utm_source=pr&utm_medium=referral&utm_campaign=pr-blog-smarthomes&utm_content=CNET [Accessed: 18 June 2019].

[2] Alton, L. Are Customers Finally Ready to Adopt Smart Home Technology? *Huffington Post*. [Online] 2017; Available from: https://www.huffpost.com/entry/are-customers-finally-ready-to-adopt-smart-home-technology_b_59e6e735e4b0e60c4aa3666f [Accessed: 18 June 2019].

[3] Zheng, S., Apthorpe, N., Chetty, M. & Feamster, N. (2018) User Perceptions of Smart Home IoT Privacy. *Proceedings of the ACM on Human-Computer Interaction - CSCW*. [Online] 2 (CSCW). Available from: doi:10.1145/3274469 [Accessed: 18 June 2019].

[4] Gennings, W. (n.d.) *Privacy Notice*. [Online]. Precious Homes. Available from: http://www.precious-homes.co.uk/privacy-policy/ [Accessed: 18 June 2019].

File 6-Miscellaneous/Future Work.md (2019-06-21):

# Future Work

## Discussion of Present Implementation

The table below shows the capabilities of WALDO that have and have not been implemented.

| No. 	| Capability                                                        	| Status                                                                                                                              	|
|-----	|-------------------------------------------------------------------	|-------------------------------------------------------------------------------------------------------------------------------------	|
| 1.  	| Makaton interpretation using machine learning                     	| **Implemented** - Interpretation of 5 signs with high accuracy and low latency.<br> **Not Implemented** - Interpretation of other Makaton signs 	|
| 2.  	| Buttons to output pre-set expressions                             	| **Implemented**                                                                                                                         	|
| 3.  	| User interface to change what expressions button presses output   	| **Not Implemented** - Strings that buttons output cannot be changed remotely, no user interface to change string output                 	|
| 4.  	| Ambient sensors to analyse and understand the user’s surroundings 	| **Not Implemented**                                                                                                                     	|
| 5.  	| Replicability of product                                          	| **Not Implemented** - Components are for prototyping use; low replicability of product                                                  	|

<Br>

## Improvements to Present Hardware

Presently, WALDO faces several challenges arising from the limited capabilities its hardware components can offer, namely:

-   The Nvidia Jetson Nano used for Makaton interpretation is a developer kit meant for rapid prototyping, and has insufficient RAM to run a larger and more complex model
    
-   The battery pack used, a Krisdonia 25000mAh battery pack, is unable to handle power surges from the Jetson when at its full computing potential, causing the battery pack to shut off power as a safety mechanism. Hence, the Jetson is run with only 3 out of its 4 cores, and at a clock speed lower than its maximum operating frequency
    
-   Several functions of WALDO have been offloaded to a Raspberry Pi to relieve computational load on the Jetson. This increases the amount of physical electronic hardware that has to be placed in the toy
    
<Br>

Using purpose-built electronic components in WALDO, with higher GPU RAM and more CPU cores or higher clock speeds, would obviate the need for two embedded devices to be present, reducing the physical space needed within the toy for electronic hardware and reducing the chance of failure of one of the components. In addition, using an appropriate battery, instead of a battery pack with a built-in safety mechanism, would allow computation to be performed at the embedded device’s full potential. A safety mechanism with a higher threshold could be used with the battery to ensure safety is not compromised.

The external physical components of WALDO could also stand to be improved. Improvements include sewing the electronic hardware onto the cotton of the device to improve robustness against rough handling, including a zip to allow easy access to WALDO’s interior devices, sewing holes into WALDO’s exterior to allow for convenient access to ports, and adding a physical on-off switch or a camera shutter for privacy.

<Br>  

## Additional Capabilities

The first, and most apparent, area in which WALDO could stand to be improved is in increasing the number of signs it can recognise. However, this is a time-consuming process due to the lack of an online Makaton database with which to train the machine learning model. As such, the following changes could be made to the data collection process if the number of signs to be recognised is to be drastically increased.

-   Use an institutionally-supported mechanism to collect training data. One method would be to offer volunteers a small amount of cash each, while keeping it within an educational institution. Another method would be to outsource data collection to a third party, such as through the use of Amazon’s Mechanical Turk[1], an online outsourcing platform where volunteers are paid for their effort.
    
-   Using machine learning or pattern recognition to automatically preprocess videos for training. This process was hugely time-consuming when performed manually.
    
-   Sourcing data from around the world, instead of only within the UK, to improve robustness of sign recognition
    
<Br>

Another capability that could be integrated into WALDO’s Makaton interpretation is the ability to learn on-the-go. Presently, WALDO uses a pre-trained model and does not retain user data for additional training. If WALDO is used by an individual user for an extended period of time, on-the-go learning could be implemented to enable predictions to improve over time.

However, implementing such a feature on WALDO faces several problems, which are not insurmountable. Firstly, there would have to be a mechanism by which the user labels the signs he is performing. This could be done through a feedback system, whereby the user provides positive or negative feedback to WALDO based on whether the prediction is correct. This feedback mechanism would in turn have to be implemented. Secondly, on-the-go learning raises a privacy concern as the user’s data would have to be stored, and may have to be uploaded to a remote server if WALDO does not have sufficient computing power to train the machine learning model. This could be addressed by clearer privacy guidelines on WALDO’s use and strict encryption protocols.

A user interface to change the expressions WALDO outputs when its buttons are pressed has not been implemented. Since both the Pi and the Jetson have Internet connectivity, implementing this function should be straightforward; the interface could either be a webpage or a phone app. The user (or carer) would change the expression to be output, which would in turn change the string passed into the IBM Watson text-to-speech software.

Ambient sensors to analyse and understand the user’s environment have yet to be implemented. These sensors could be integrated with the Pi, sending information via the GPIO pins or tailor-made breakout boards and stored on the Pi for later analysis by medical professionals. Understanding the environment and possible risk factors is important in caring for people with learning disabilities[2], hence sensors that could be implemented include ambient light, sound and temperature sensors.

<Br>

## Bibliography

[1] Amazon. Overview. *Amazon Mechanical Turk.* [Online] Available from: https://www.mturk.com/ [Accessed: 18 June 2019].

[2] National Institute for Health and Care Excellence. (2015) NG11. *Challenging behaviour and learning disabilities: prevention and interventions for people with learning disabilities whose behaviour challenges.* NICE.

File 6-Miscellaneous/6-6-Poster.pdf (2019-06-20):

Choice of Makaton Signs
5 Makaton signs chosen based on the following considerations: Recommendations from Precious Homes, a care home for people with learning disabilities and other needs
Static and moving signs to demonstrate device capabilities

Figure 2: 5 Makaton signs chosen for implementation

Volunteers¹ found around the Imperial College South Kensington campus – videos of volunteers performing Makaton signs were recorded for dataset

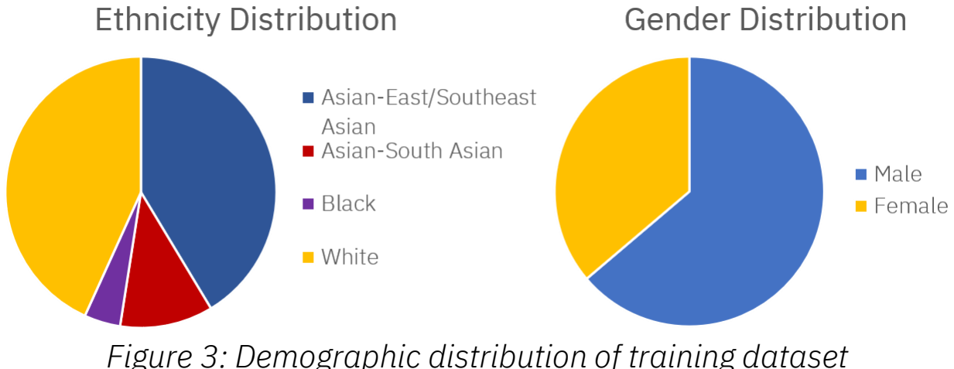
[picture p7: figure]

Figure 3: Demographic distribution of training dataset

The diversity of the training dataset was maximised to ensure robustness when used by different users

Machine Learning employed to interpret these Makaton signs

1. Volunteers in this project provided their consent to the video recordings on the basis that the recordings were only to be used for this project and would be deleted at the end of the project.

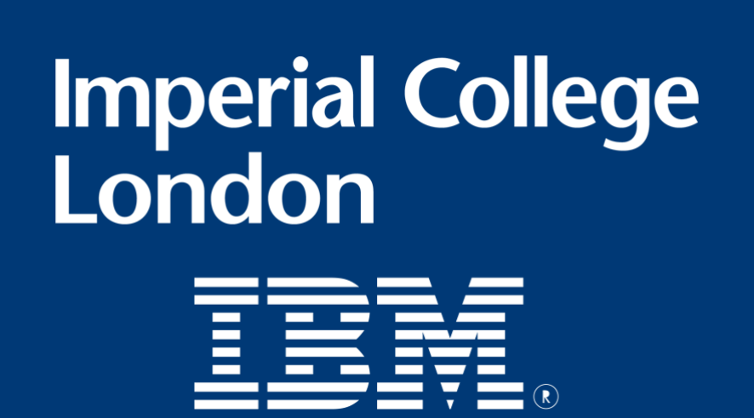
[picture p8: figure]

# Joshua Rizal Chan, Lua Ying Hao, Ng Yi Song, Patrick John Chia, Yeow En Kai Joel Department of Electrical and Electronic Engineering, Imperial College London

What is WALDO ? | Makaton Sign Language Recognition with Machine Learning

Machine learning implemented on Nvidia Jetson Nano – contains GPU optimised for running convolution operations required in machine learning
To limit computational overhead on the Jetson Nano, a Raspberry Pi performs all other device functions – buttons, speakers and sensors (excluding camera) IBM Watson Text-to-Speech implemented on Pi, with output via connected speakers
Jetson and Pi connected using GPIO pins
Pi → Jetson: Ultrasonic sensor information, to start machine learning detection of Makaton signs
Jetson → Pi: Action detected by machine learning model
Power source: Portable power bank used as a power source to ensure portability while fulfilling laptop-grade requirements of Jetson

# WALDO Hardware

Makaton
Increase the number of signs the device can recognise
Implement broader-scale, institutionally supported method of data collection to increase size and diversity of dataset
Device sensors
Integrate ambient sensors that provide carers with a fuller understanding of the user’s environment, to facilitate better detection of possible risk factors
Create a plug-and-play system for sensors to make WALDO an easily upgradeable and expandable system as user needs adapt
Improve manufacturability of product by designing suitable physical components
Use purpose-built electronic components to improve performance and power consumption

# Future Work

We would like to thank:
Dr Steve Wright, for his invaluable guidance and encouragement throughout the project
Louise Cooper, John McNamara & Emily Larkin from IBM for their clear direction and unwavering support in the implementation of this project Precious Homes, for supporting this project by providing valuable insight into the use of Makaton, as well as training videos
Vic, May & Amine at the teaching labs, for their untiring technical support All who volunteered their time to help us in the collection of training data

# Acknowledgements

# Conclusion

# Methodology

# Watson Assisted Living Device – WALDO

A cute and endearing device that performs low latency Makaton Sign Language Recognition and Vocalisation using Machine Learning
Contains on-device buttons that the user can press to vocalise pre-set phrases in a quick and convenient manner
Has customisable on-board ambient sensors to help the carer or medical professionals to understand the environmental conditions of the user

Care homes for people with learning difficulties face high staff turnover and staffing costs
Training staff to use Makaton is expensive and time-consuming
WALDO aims to provide a streamlined, cost-effective way for care homes to provide high-quality care for Makaton users by easing communication

Figure 1: WALDO’s core capabilities

# Why WALDO ?

Classification Problem : 6 Classes –– 5 Makaton Gestures + 1 No Action Class
Input | : 30 contiguous frames, each of dimension 640x480x3 pixels, x ∈ ℝ³⁰×640×480×3
Hypothesis | : ℎ ∈ H where H is the set of possible hypothesis
Output | : yො = ℎ x = [yො1, yො2, … , yො6]

T∈ ℝ⁶x1
, predicted probability of each class yොn given input x
Loss Function | : Categorical Cross Entropy, to heavily penalise confident but wrong predictions.
l | ℎ x | = − ෍
| | c=1

c= 6
yc

log yොc

where yc

is binary (0 or 1) and indicates if class c is the correct classification given observation x.
Aim | : Obtain best model g such that

g = argmin
ℎ∈H

1
N

෍

i=1

N
l ℎ xi

where N is the size of the training set with xi

the inputs from the training set.

# Deep Neural Network Architecture

# Model Performance

# Model Evaluation

Important to capture spatio-temporal information for accurate gesture recognition
Proposed architecture achieves this by using both 3D Convolution (Conv3D) and Long Short Term Memory (LSTM)
Conv3D performs convolution not only along the height and width domain but also the temporal domain of the input frames – both spatial and temporal features learned and passed into the LSTM
LSTM further studies the time-evolution of the spatio-temporal features captured before making a decision on the gesture recorded

The main capability of WALDO, the interpretation of Makaton signs, has been successfully implemented with low latency
Machine learning for sign language interpretation is feasible and shows great potential for further expansion
Given more time, WALDO’s capabilities can be extended, and its present hardware streamlined, to provide a more holistic system of care for its user Figure 4: Deep Neural Network Architecture

Figure 5: 3D Convolution

2

Figure 6: LSTM Cell

Figure 7: Evolution of model accuracy

Figure 8: Principle Component Analysis (PCA) plot of compressed feature vectors

Visualisation of 512-dimension vector space with 2 dimensions using PCA Clear clustering of each class can be observed
Distance between features from actions Home, Good & Sorry closer than desired, but explainable given innate similarity

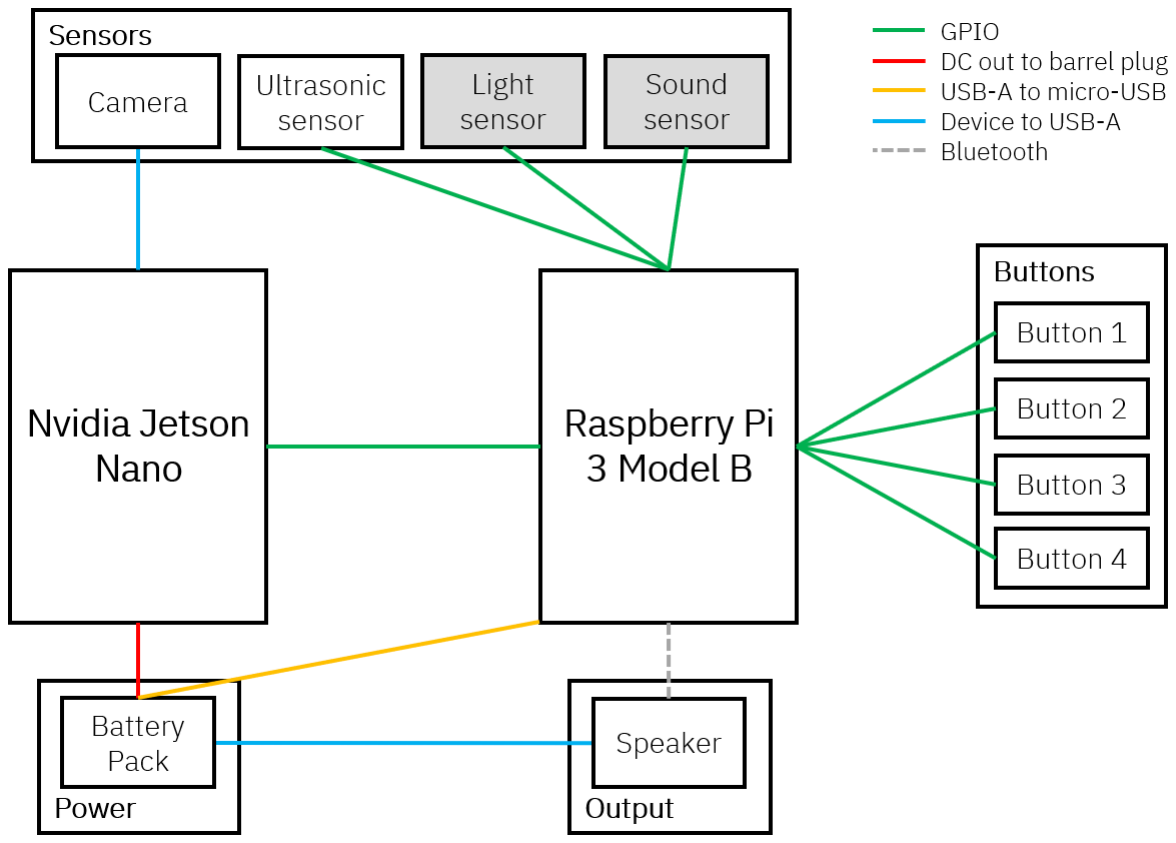
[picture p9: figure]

Figure 9: Diagram of device hardware and connections (gray sensors not implemented)

# Additional Considerations

Network compressed sufficiently for edge computing on Jetson
Reduced latency (~1.0s)
10x speed up in throughput (~9Hz)
To | accommodate | GPU | RAM
limitations – only 2.5GB available
Data | Augmentation | enables | sign
recognition from anywhere in the frame

Figure 11: Visualisation of effect of model compression on RAM usage
Figure 10: Example of data augmentation (original at top left, all other images randomly modified)
2. Tran, D., Bourdev, L., Fergus, R., Torresani, L., et al. (2015) Learning Spatiotemporal Features with 3D Convolutional Networks. 2015 IEEE International Conference on Computer Vision (ICCV).

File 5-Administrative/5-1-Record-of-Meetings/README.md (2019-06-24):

5.1 Overview of Meetings
====================

Over the course of this project, meetings were scheduled with the following regularity:

* Video conference meetings with IBM supervisors every Friday at 2pm
* Fortnightly meetings with academic supervisor, Dr Steve Wright, on Wednesday at 2pm

<Br>
  
Minutes for meetings with IBM and academic supervisors were taken and are included in this folder; these minutes include a record of decisions taken and their rationale. The calendar below presents a timeline of the project, and a frame of reference for understanding the meeting minutes.

<Br>

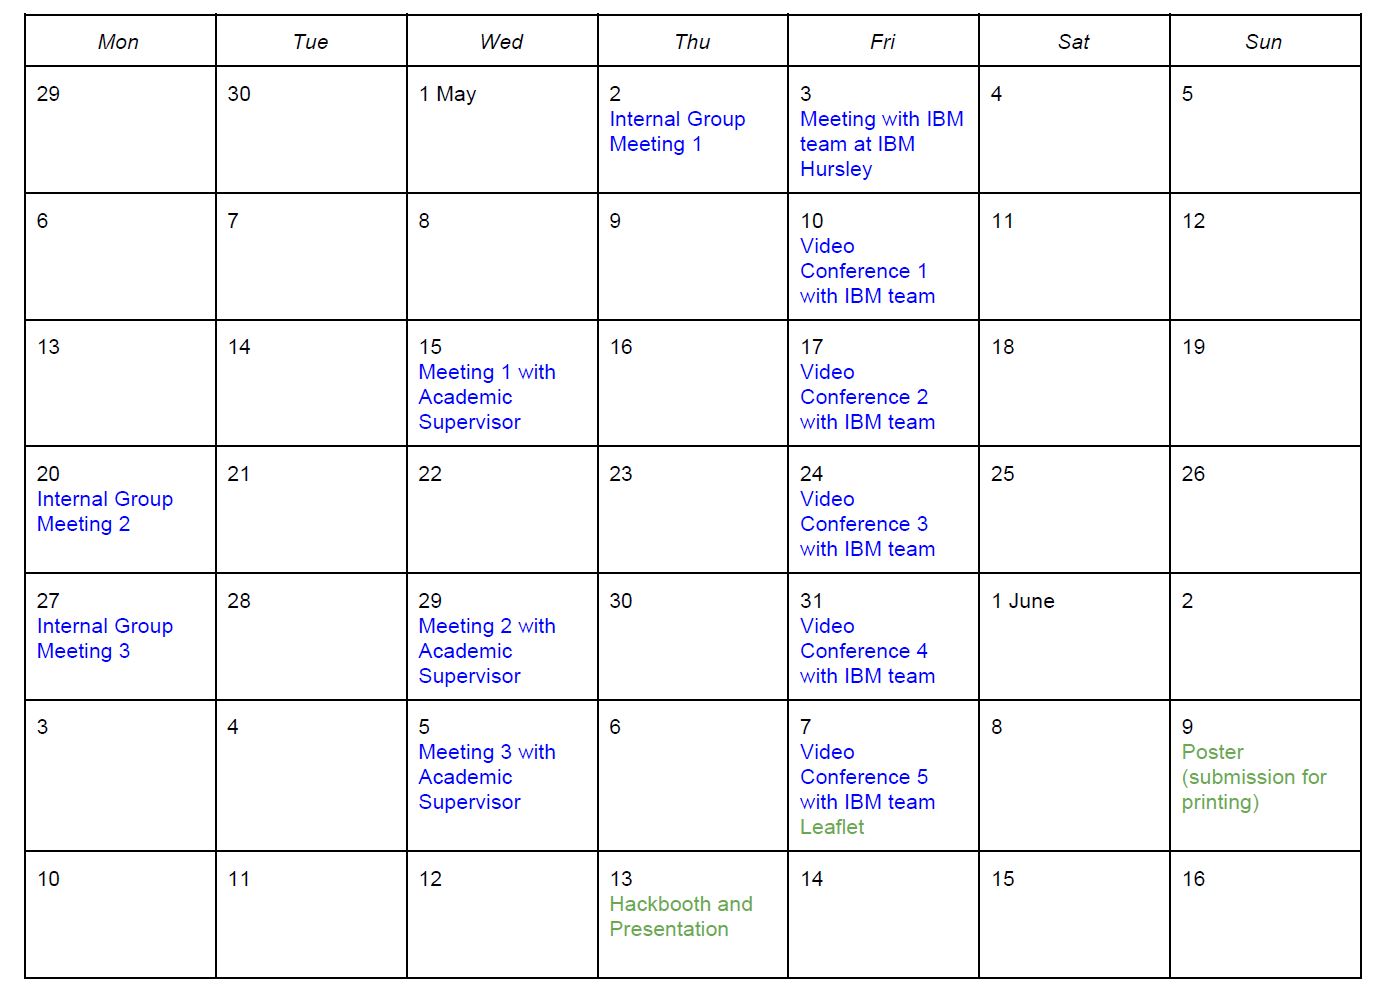
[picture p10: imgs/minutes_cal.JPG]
Calendar of meeting minutes


<Br>
  
Meetings where minutes were taken are recorded in blue, deadlines for deliverables are recorded in green.



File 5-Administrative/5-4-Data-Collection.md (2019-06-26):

5.4 Data Collection
===============

Go To
------
* 5.4.1 [Group Members](#541-group-members)
* 5.4.2 [Data Privacy](#542-data-privacy)
* 5.4.3 [Method of Data Collection](#543-method-of-data-collection)
* 5.4.4 [Ethnic Distribution](#544-ethnic-distribution)

5.4.1 Group Members
--------------

Initially, data collection was conducted internally, with three members of the group acting as signers. The initial dataset, encompassing all 5 actions, has the following characteristics:

 -   3 signers (3 members of group)
 -   20 backgrounds
 -   9 angles (three heights, three directions -- left, straight and right)

This initial dataset consisted of 2700 videos. However, it was quickly discovered that the low amount of diversity in this dataset would be severely insufficient to train a machine learning model robust enough to interpret signs from a range of signers. Furthermore, all three group members were of the same ethnicity (Asian -- Chinese). Hence, volunteers were required as signers for further data collection.

5.4.2 Data Privacy
-----------

In order to keep the project ‘internal’ for now, the decision was taken to only film volunteers around the Imperial College London campus at South Kensington. As such, only staff and students of Imperial College were filmed as volunteers. Before filming any volunteer, the purpose of the project and the reasons for filming were explained. Filming would then take place only if he or she gave their consent to the video recordings on the basis that the recordings were only to be used for this project and would be deleted at the end of the project.

5.4.3 Method of Data Collection
------------------------

It soon became clear that in order to have an accurate and robust neural network model, a significantly larger amount of data had to be collected. In other words, the gathering of data had to be extended beyond the three group members. The dataset collected had to comprise of different people of varying ethnicity, filmed under different lighting conditions and backgrounds.

Volunteers were randomly found and filmed around the Imperial College London campus at South Kensington. Each volunteer would be filmed 5 times, corresponding to the 5 actions. In order not to demand too much of the volunteer, each volunteer was only filmed from a single angle- from a straight direction and a middle height with the volunteer stood approximately 2 metres from the camera. This angle and distance was chosen as the approximate height at which WALDO would eventually be placed at. A total of 162 volunteers were filmed.

5.4.4 Ethnic Distribution
-------------------

The dataset has the following ethnic composition(1).

| Ethnicity                  	| Number 	| Percentage 	|
|----------------------------	|--------	|------------	|
| Asian-East/Southeast Asian 	| 67     	| 41.4       	|
| Asian-South Asian          	| 18     	| 11.1       	|
| Black                      	| 7      	| 4.32       	|
| White                      	| 70     	| 43.2       	|

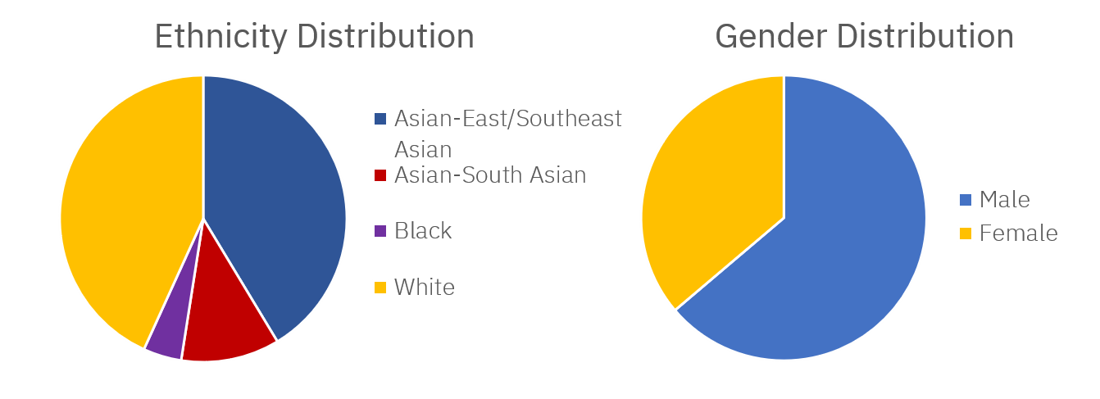
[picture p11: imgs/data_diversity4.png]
Enthicity and Gender Distributions Ethnicity and Gender Distributions


> (1) A more detailed ethnic breakdown is not feasible as volunteers were not asked for information on their ethnicity when data was collected.

This compares well with Imperial College’s ethnic composition(2), shown below.

| Ethnicity                                          	| Postgraduate (PG)   	| Undergraduate (UG)   	| PG%  	| UG%  	|
|----------------------------------------------------	|------	|------	|------	|------	|
| White                                              	| 2310 	| 1177 	| 43.4 	| 40.1 	|
| Black or Black British – African, Caribbean, Other 	| 168  	| 82   	| 3.2  	| 2.8  	|
| Asian or Asian British – Indian                    	| 293  	| 250  	| 5.5  	| 8.5  	|
| Asian or Asian British – Pakistani                 	| 69   	| 63   	| 1.3  	| 2.1  	|
| Asian or Asian British – Bangladeshi               	| 33   	| 24   	| 0.6  	| 0.8  	|
| Chinese                                            	| 1533 	| 651  	| 28.8 	| 22.2 	|
| Other Asian background                             	| 317  	| 212  	| 6.0  	| 7.2  	|
| Mixed Ethnicities                                  	| 208  	| 132  	| 3.9  	| 1.3  	|
| Arab                                               	| 172  	| 39   	| 3.2  	| 1.3  	|
| Other ethnic background                            	| 79   	| 33   	| 1.5  	| 1.1  	|
| Not known                                          	| 16   	| 201  	| 0.3  	| 6.8  	|
| Information refused                                	| 119  	| 74   	| 2.2  	| 2.5  	|

> (2) Acquired from a freedom of information request, accessible online at [https://www.whatdotheyknow.com/request/statistics_on_ethnicity](https://www.whatdotheyknow.com/request/statistics_on_ethnicity)

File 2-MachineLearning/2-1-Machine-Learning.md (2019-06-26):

2.1 Machine Learning / Deep Learning
===

This section details the experimentation phase and the deployment phase of the Deep Learning model. The Deep Learning model forms the backbone of WALDO as it performs the crucial task of Makaton Sign Recognition. This section includes the key design decisions and the rationale behind them.

## Go To
* 2.1.1 [Model Development History and Evolution](#211-model-development-history-and-evolution)
* 2.1.2 [Model Deployment](#212-model-deployment)
* 2.1.3 [Conclusion](#213-conclusion)

## 2.1.1 Model Development History and Evolution

This section explains and provides the performance of the various Deep Learning models that were experimented with to determine the best model for Makaton Sign Recognition. In addition it provides details about the dataset used in this phase.

#### 2.1.1.1 Dataset
In the experimentation phase, the [Jester Dataset](https://20bn.com/datasets/jester/v1#download) was utilised. 6 (Swiping Left, Swiping Down, Thumb Up, Drumming Fingers, Sliding Two Fingers Left, No gesture) out of the 26 Gestures available were selected and used througout all experiments. 

The Jester Dataset was used whilst the team was still building the Makaton Sign dataset. The use of a prebuilt dataset during the experimentation phase was critical as the dataset is large and diverse enough, providing suffucient data for Deep Learning. This lends to two important aspects in Machine Learning.

1. Training: It is vital to have sufficient data for the training set to improve the model's ability to generalise.

2. Validation: A validation set which the model has not been trained on is used to measure how well the model has generalised. A large and sufficiently diverse validation set will ensure that the validation accuracy/loss measured is a good proxy of the true accuracy/loss of the model on unseen data.

Therefore, the Jester dataset provides confidence in the results of the experiments which was vital for determining which model was best suited for the task of Gesture Recognition.

#### 2.1.1.2 Experimental Results
The plot below gives a summary of the performance (accuracy) of the various models. Each model is also described below.

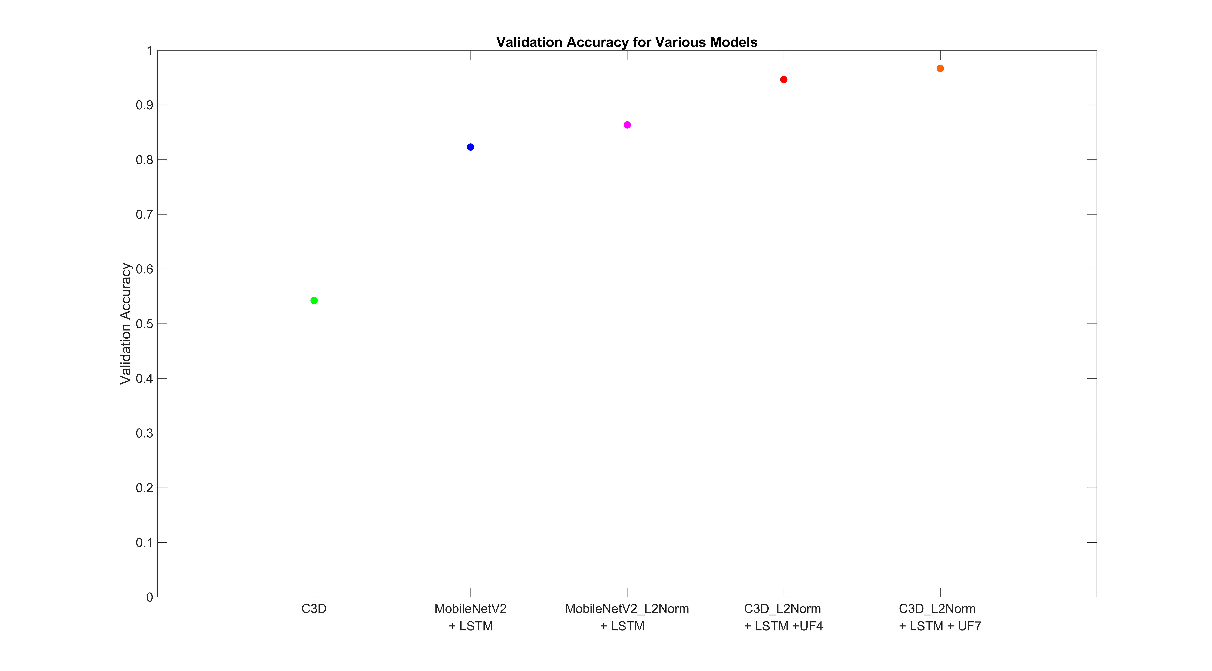
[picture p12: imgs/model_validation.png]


#### 1)<space> C3D

The model employs the use of 3D Convolution Networks to capture spatio-temporal features that are crucial in classifying Makaton signs that are non-static. 

The keras implementation for C3D can be obtained [here](https://gist.github.com/albertomontesg/d8b21a179c1e6cca0480ebdf292c34d2). As the model is large, end-to-end training is time consuming. As such pre-trained weights, also available through the above link, were utilised. The final dense layer was modified to 6 outputs since 6 classes are required. The layer `fc7` and final dense layer were unfrozen, with all other layers frozen.

Model achieved a validation accuracy of <b>54.25%</b> on 5+1(No action) classes on [20BN-Jester](https://20bn.com/datasets/jester) dataset.

Refer to [C3D Paper](https://arxiv.org/pdf/1412.0767.pdf) for more details

#### 2)<space> MobileNetV2 + LSTM

The model employs the use of 2D Convolution Networks pre-trained on [Imagenet](https://www.kaggle.com/c/imagenet-object-localization-challenge) and gives us a quick and lightweight method to capture spatial features. Spatial features learnt are then passed into a Long Short Term Memory(LSTM) module to further study its study time evolution.

Model achieved a validation accuracy of <b>82.32%</b> on 5+1(No action) classes on 20BN-Jester dataset.

Refer to [CNN+LSTM Paper](https://static.googleusercontent.com/media/research.google.com/en//pubs/archive/43455.pdf) for more details

#### 3)<space> MobileNetV2_L2Norm + LSTM

Just like <b>MobileNetV2 + LSTM</b>, this model employs the use of 2D Convolution Networks pre-trained on Imagenet. For this model, the learnt spatial features for each frame are L2 normalised to become vectors of unit length before passing them into the LSTM module. 

Model achieved a slight boost in validation accuracy to <b>86.35%</b> on 5+1(No action) classes on 20BN-Jester dataset.

#### 4)<space> C3D_L2Norm + LSTM + UF4

The model employs the use of 3D Convolution Networks to capture spatio-temporal features that are crucial in classifying Makaton signs which are non-static. The learnt spatio-temporal features are then passed into the LSTM to further study its time evolution. Learning not only spatial but temporal features as well allowed the representations of makaton sings to be better captured. This facilitated a huge improvement over the <b>MobileNetV2_L2Norm + LSTM</b> model.

Model achieved a validation accuracy of <b>94.64%</b> on 5+1(No action) classes on 20BN-Jester dataset.

Refer to [C3D+LSTM Paper](https://arxiv.org/pdf/1412.0767.pdf) for more details

#### 5)<space> C3D_L2Norm + LSTM + UF7

This is the same model as the model <b> C3D_L2Norm + LSTM + UF4 </b> above but with the final 7 layers unfrozen(3 more than UF4). This allowed the model to better learn the patterns on the Jester dataset as compared to just using the pre-trained weights that are not tuned specifically to Jester.

Model achieved a validation accuracy of <b>96.69%</b> on 5+1(No action) classes on 20BN-Jester dataset.

## 2.1.2 Model Deployment

The experimental phase allowed the team to determine which model was best suited for the task of Gesture Recognition. Based on the above results, the C3D + L2Norm + LSTM Models (Models 4 and 5) were shown to be superior over the other models. However, there were still 2 challenges to overcome.

#### 2.1.2.1 Deployment of Model on Jetson Nano

The model used in the experiments consisted of the full C3D model. In total, together with the LSTM componenet, the proposed model had \~ 30M Parameters. The model was run on the Jetson Nano and had an inferece rate of \~1.25 inferences/s. In other words, it could only run at 0.8 Frames Per Second (FPS). This is far too slow for real-time detection with video frames comining from a camera stream. Furthermore, with that many paramters, end-to-end training with all layers unfrozen will take extremely long.

It was therefore crucial to reduce the model size. This was achieved by tweaking the model in several ways.

Firstly, considering that 3D Convolution is computationally expensive, the last 2 3D Convolutional layers were removed.

Another aspect of convolution that can lead to computational savings is the number of output filters of the convolution operation. Theoretically, the computational complexity of each layer should scale linearly with the number of output filters. In reality, the computational savings may not be exactly linear due to optimizations applied by cuDNN on GPU hardware. Nevertheless, with the goal of improving inference rate, the number of filters for first 4 Convlutional layers was reduced by a factor of 2 and the by a factor of 4 for the last 2 layers.

Lastly, the dimensions (Depth x Width x Height x # Filters) of the input to a convolution is another factor that determines its speed. The input layer has dimensions (30,112,112,3) and the input convolution in the original C3D model has strides (1,1,1) (D,W,H), padding set to 'same' and 64 output filters. Therefore it's output would be of shape (30,112,112,64). The sheer size of this layer will eventually trickle down the rest of the model. Therefore, the first convolutional layer was modified to have strides (1,2,2) i.e stride 1 along the temporal domain, and stride 2 along the spatial domain, and the number of output filters halved, reducing its output to shape (30,56,56,32), a reduction by a factor of 8. Since the convolution kerenel is of size 3x3, information from the input is not completely lost as there are still regions of overlap despite a stride of 2x2.

After applying the above modifications, the model was observed to have \~3M parameters. The model was then run on the Jetson Nano and an infernece rate of \~0.125 inferences/s or 8 FPS was observed - sufficient for smooth, real-time gesture detection.

To test the limits of the minimized model, it was trained with the training data (118,562 samples) from the Jester Dataset which has 27 classes. 80% of the training data was used as the training set and 20% of the training data was used as the validation set. The model was trained for 5 epochs and it had obtained a training accuracy of 88% and a validation accuracy of 87%. The team does believe that the model had overfitted yet (meaning that it was possible that the training and validation accuracy could still rise), but this provided sufficient evidence of the models’ capacity and capabilities. 

Below is a high-level overview of the final model :

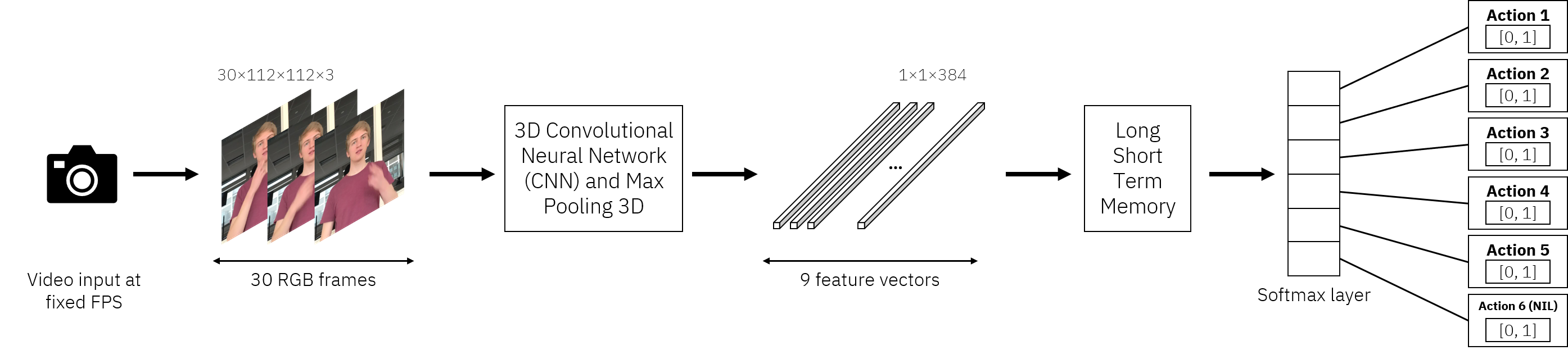
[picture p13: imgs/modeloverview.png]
 

#### 2.1.2.2 Training Model with Limited Dataset

Given the time constraints, the collected dataset was not as large and diverse as that of the Jester Dataset. The dataset collection process is detailed [here](https://github.com/patrickjohncyh/ibm-waldo/blob/master/5-Administrative/5-4-Data-Collection.md). The team was only able to collect a total of 175 videos per class (5 in this case) for our training set. Of the 175 videos, 70 of them were of the three group members tasked with data collection, leaving 105 videos per class that is of random people. For our validation set, we had 50 videos per class, all of which are of random people.

The model was trained on our dataset with 6 classes (5 actions + 1 no gesture). It was able to achieve a training accuracy of 98.8% and a validation accuracy of 91.6%. This appeared to be a very positive result, but the team was wary of the fact that our validation set had only a total of 300 samples.

Data augmentation was deployed to circumvent the problem of limited data. Data augmentation is a technique to artificially create new training data from existing training data. The same affine transformations were applied to all the frames of a given video sample that is 30 frames in length. This involved random translation (+/- 20% in x and y axis) , scaling (80%-120%), rotation (+/- 5 deg) and shear (+/- 5 deg) within the ranges specified. In addition, contrast normalization (0.75-1.5) and additive gaussian noise were also introduced.

Additionally, data from the Jester Dataset was also integrated into the final model. On top of the augmented data, the model was also trained with non-conflicting actions (i.e there is a _Thumb Up_ in Jester which clashes with the _Good_ action). Having more data from both our augmented dataset and the Jester dataset would enable the model to better learn the important spatio-temporal features for gesture recognition. Having additional gestures (classes) from Jester would guide the model into learning better representations of the gestures and to also focus on the salient parts of the data that are most pertinent to recognising gestures.

## 2.1.3 Conclusion

The model is able to achieve a peak validation accuracy of 89.5%. Whilst at first glance, this may seem like a downgrade from the 91.6% obtained without augmentation, it is important to point out that the 89.5% validation accuracy was obtained over 26 classes (3 times more classes that before) and also on substantially more data (22,462 samples). This gave confidence that the validation loss and accuracy reflects well the model’s out of sample performance.

Below is the plot of the final learning curve. The model used is **c3d_super_lite**, trained for 30 Epochs on the Jester Dataset combined with the collected dataset of 5 Makaton Signs. Augmentation was applied so the ratio of number of samples from each class (except 'Doing other things') was close to 1:1 across both datasets. **Adam** optimiser was used with **categorical crossentropy** as loss. The best model had a validation loss of 0.3683 and a validation accuracy of 0.9038.

Actions used:

`(M)` indicates that the action was one of the 5 Makaton Signs.

```
['Dinner' (M) , 'Doing other things', 'Good' (M), 'Home' (M), 'No' (M), 'No gesture', 'Pulling Hand In', 'Pulling Two Fingers In', 'Pushing Hand Away', 'Pushing Two Fingers Away', 'Rolling Hand Backward', 'Rolling Hand Forward', 'Sorry' (M), 'Sliding Two Fingers Down', 'Sliding Two Fingers Left', 'Sliding Two Fingers Up', 'Stop Sign', 'Swiping Down', 'Swiping Left', 'Swiping Up', 'Turning Hand Clockwise', 'Turning Hand Counterclockwise', 'Zooming In With Full Hand', 'Zooming In With Two Fingers', 'Zooming Out With Full Hand', 'Zooming Out With Two Fingers']
```

The training log has also been provided in this directory.

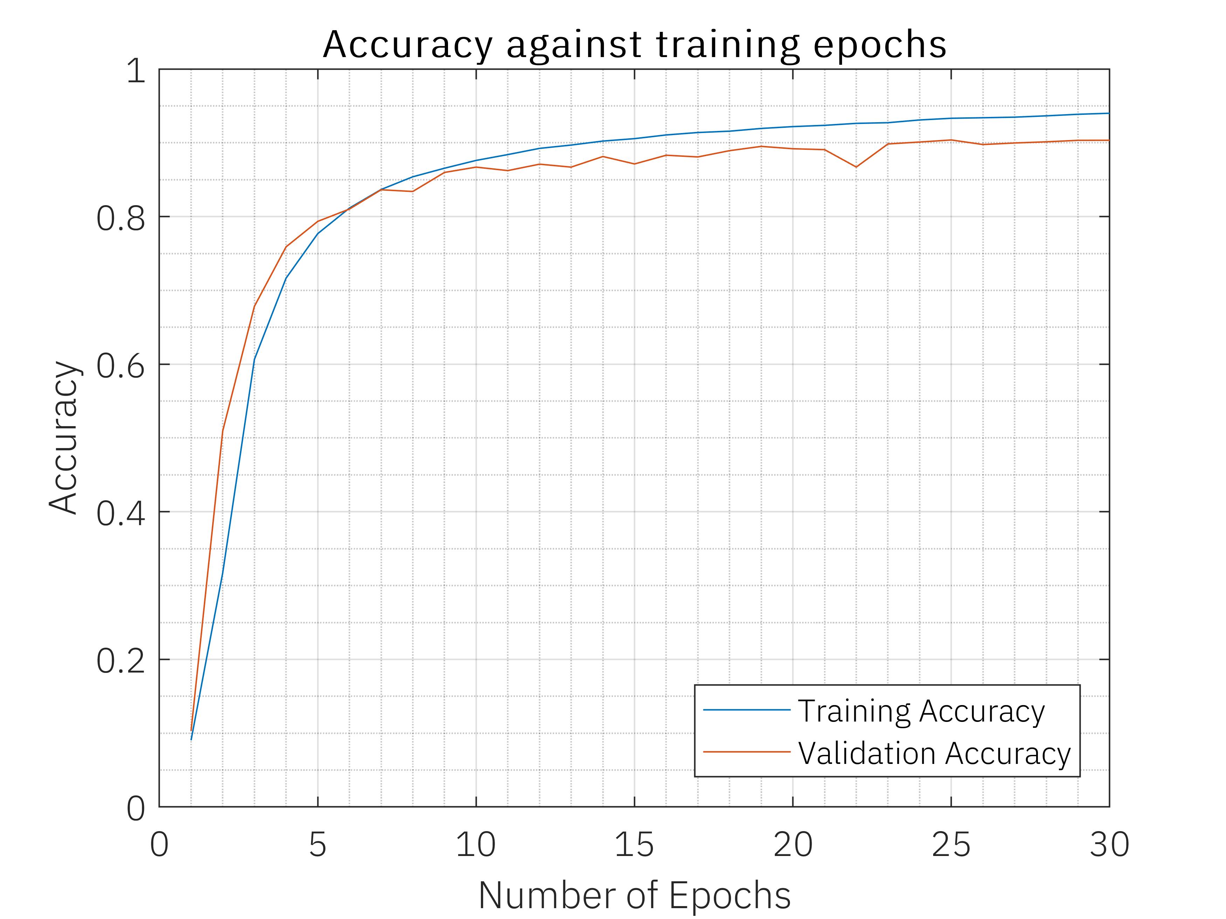
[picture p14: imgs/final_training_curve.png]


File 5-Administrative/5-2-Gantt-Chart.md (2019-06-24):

5.2 Gantt Chart
============

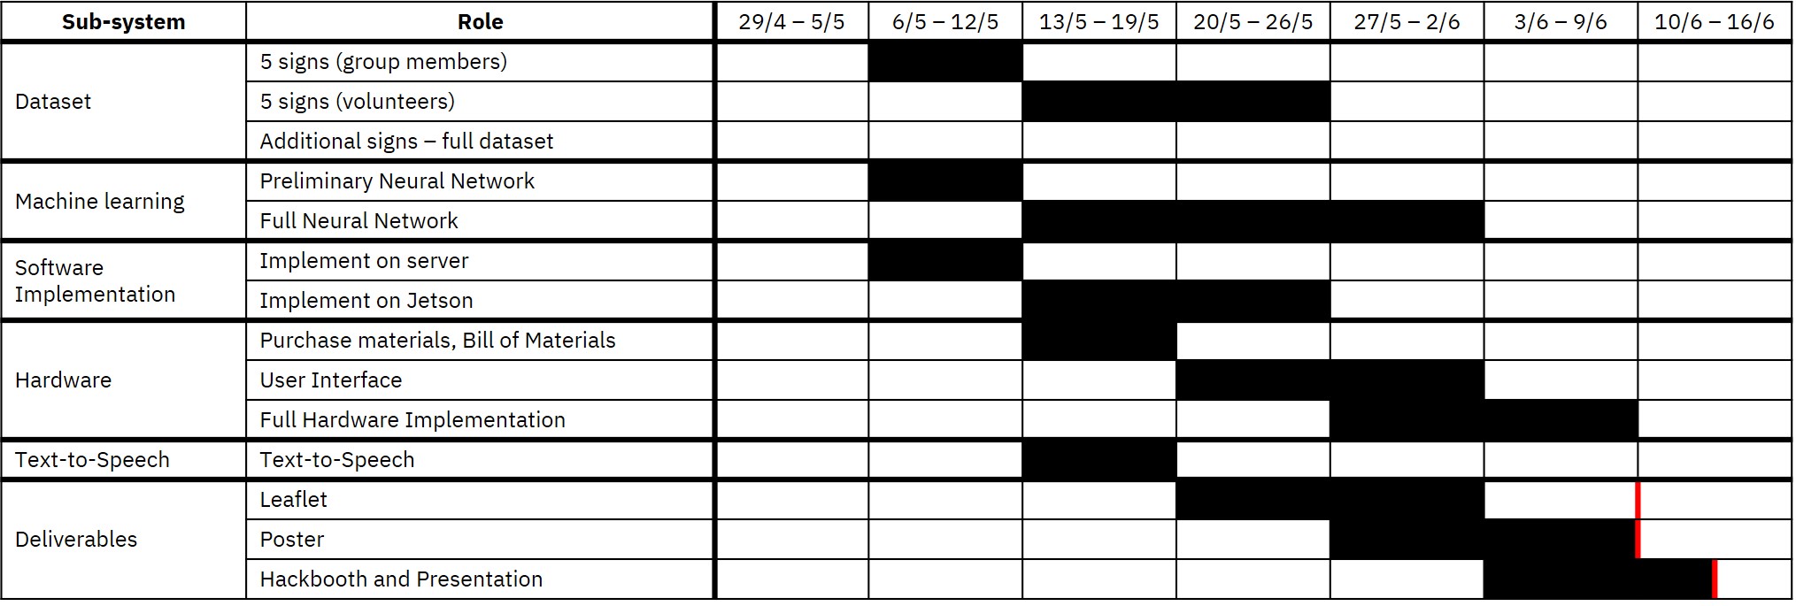
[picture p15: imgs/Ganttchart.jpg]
Gantt chart


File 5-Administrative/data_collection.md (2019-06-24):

Data Collection
===============

Go To
------
* [Group Members](#group-members)
* [Data Privacy](#data-privacy)
* [Method of Data Collection](#method-of-data-collection)
* [Ethnic Distribution](#ethnic-distribution)

Group Members
--------------

Initially, data collection was conducted internally, with three members of the group acting as signers. The initial dataset, encompassing all 5 actions, has the following characteristics:

 -   3 signers (3 members of group)
 -   20 backgrounds
 -   9 angles (three heights, three directions -- left, straight and right)

This initial dataset consisted of 2700 videos. However, it was quickly discovered that the low amount of diversity in this dataset would be severely insufficient to train a machine learning model robust enough to interpret signs from a range of signers. Furthermore, all three group members were of the same ethnicity (Asian -- Chinese). Hence, volunteers were required as signers for further data collection.

<Br>
 
Data Privacy
-----------

In order to keep the project ‘internal’ for now, the decision was taken to only film volunteers around the Imperial College London campus at South Kensington. As such, only staff and students of Imperial College were filmed as volunteers. Before filming any volunteer, the purpose of the project and the reasons for filming were explained. Filming would then take place only if he or she gave their consent to the video recordings on the basis that the recordings were only to be used for this project and would be deleted at the end of the project.

<Br>

Method of Data Collection
------------------------

It soon became clear that in order to have an accurate and robust neural network model, a significantly larger amount of data had to be collected. In other words, the gathering of data had to be extended beyond the three group members. The dataset collected had to comprise of different people of varying ethnicity, filmed under different lighting conditions and backgrounds.

Volunteers were randomly found and filmed around the Imperial College London campus at South Kensington. Each volunteer would be filmed 5 times, corresponding to the 5 actions. In order not to demand too much of the volunteer, each volunteer was only filmed from a single angle- from a straight direction and a middle height with the volunteer stood approximately 2 metres from the camera. This angle and distance was chosen as the approximate height at which WALDO would eventually be placed at. A total of 162 volunteers were filmed.

<Br>

Ethnic Distribution
-------------------

The dataset has the following ethnic composition(1).

| Ethnicity                  	| Number 	| Percentage 	|
|----------------------------	|--------	|------------	|
| Asian-East/Southeast Asian 	| 67     	| 41.4       	|
| Asian-South Asian          	| 18     	| 11.1       	|
| Black                      	| 7      	| 4.32       	|
| White                      	| 70     	| 43.2       	|

<Br>

Enthicity and Gender Distributions Ethnicity and Gender Distributions

> (1) A more detailed ethnic breakdown is not feasible as volunteers were not asked for information on their ethnicity when data was collected.

<Br>

This compares well with Imperial College’s ethnic composition(2), shown below.

| Ethnicity                                          	| Postgraduate (PG)   	| Undergraduate (UG)   	| PG%  	| UG%  	|
|----------------------------------------------------	|------	|------	|------	|------	|
| White                                              	| 2310 	| 1177 	| 43.4 	| 40.1 	|
| Black or Black British – African, Caribbean, Other 	| 168  	| 82   	| 3.2  	| 2.8  	|
| Asian or Asian British – Indian                    	| 293  	| 250  	| 5.5  	| 8.5  	|
| Asian or Asian British – Pakistani                 	| 69   	| 63   	| 1.3  	| 2.1  	|
| Asian or Asian British – Bangladeshi               	| 33   	| 24   	| 0.6  	| 0.8  	|
| Chinese                                            	| 1533 	| 651  	| 28.8 	| 22.2 	|
| Other Asian background                             	| 317  	| 212  	| 6.0  	| 7.2  	|
| Mixed Ethnicities                                  	| 208  	| 132  	| 3.9  	| 1.3  	|
| Arab                                               	| 172  	| 39   	| 3.2  	| 1.3  	|
| Other ethnic background                            	| 79   	| 33   	| 1.5  	| 1.1  	|
| Not known                                          	| 16   	| 201  	| 0.3  	| 6.8  	|
| Information refused                                	| 119  	| 74   	| 2.2  	| 2.5  	|

<Br>

> (2) Acquired from a freedom of information request, accessible online at [https://www.whatdotheyknow.com/request/statistics_on_ethnicity](https://www.whatdotheyknow.com/request/statistics_on_ethnicity)

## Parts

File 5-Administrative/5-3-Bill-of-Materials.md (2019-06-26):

# 5.3 Bill of Materials

The following table shows the various components bought and used in the assembly of WALDO:

| Item                                 	| Product Description                                                                                                                                                                  	| Manufacturer    	| Quantity 	| Total Price / £ 	|
|--------------------------------------	|--------------------------------------------------------------------------------------------------------------------------------------------------------------------------------------	|-----------------	|----------	|-----------------	|
| Elephant Stuffed Toy                 	| Fuddlewuddle Elephant, Medium- H23 cm                                                                                                                                                	| Jellycat        	| 1        	| 18.50           	|
| Jetson Nano                          	| NVIDIA Jetson Nano Developer Kit                                                                                                                                                     	| NVIDIA          	| 1        	| 99.00           	|
| 64GB Micro SD Card for Jetson        	| INMSDX64G10-90U1 - 64GB Ultima Pro Class 10 MicroSDXC Memory Card with SD Adaptor 90MB/s                                                                                             	| Integral        	| 1        	| 8.95            	|
| Cooling Fan for Jetson               	| Noctua NF-A4x20 5V PWM, Premium Quiet Fan, 4-Pin, 5V Version (40x20mm, Brown)                                                                                                        	| Noctua          	| 1        	| 13.16           	|
| Power Adapter for Jetson             	| RS PRO, 20W Plug In,Power Supply 5V, 4A, Level VI Efficiency, 1 Output Switched Mode Power Supply, 3-Pin UK                                                                          	| RS PRO          	| 1        	| 13.62           	|
| Webcam                               	| Logitech C920 HD Pro Webcam                                                                                                                                                          	| Logitech        	| 1        	| 89.99           	|
| Wifi Dongle                          	| EW-7811UN - N150 Wi-Fi Nano USB Adaptor                                                                                                                                              	| Edimax          	| 1        	| 7.62            	|
| Power Bank                           	| Krisdonia Laptop Power Bank 25000mAh Portable Charger with Type-C Port + DC Port + Dual USB (QC3.0 Quick Charge) for Laptop, Tablet, Cell phone, Macbook, Camera, Projector and more 	| Krisdonia       	| 1        	| 98.00           	|
| Raspberry Pi                         	| Raspberry Pi 3 Model B                                                                                                                                                               	| Raspberry Pi    	| 1        	| 34.07           	|
| 8GB Micro SD Card for Raspberry Pi   	| Kingston 8GB Micro SDHC Class 4 Memory Card                                                                                                                                          	| Kingston        	| 1        	| 3.40            	|
| Speakers                             	| 00173130 - Sonic Mobil 181 2.0 PC Speakers 3W Black                                                                                                                                  	| Hama            	| 1        	| 5.49            	|
| Buttons                              	| 1825910-6: Black Button Tactile Switch, Single Pole Single Throw (SPST) 50 mA @ 24 V dc 1.4mm                                                                                        	| TE Connectivity 	| 4        	| 0.30            	|
| Ultrasonic sensor                    	| Parallax Inc 28015, PING))) Ultrasonic Distance Sensor Module                                                                                                                        	| Parallax Inc    	| 1        	| 23.24           	|
| Hook and Loop Fasteners- Velcro Tape 	| VELCRO Brand Stick On For,Fabrics Tape, 19 mm x 60 cm - White                                                                                                                        	| Velcro Brand    	| 1        	| 3.79            	|
| **Total Cost**                           	| -                                                                                                                                                                                    	| -               	| -        	| **£419.13**         	|

This amounts to a total of £419.13, which would be rather costly for mass production. The significant chunks of the cost can be attributed to Jetson Nano Developer Kit, the Raspberry Pi, the portable power bank and the webcam. However, a lot of the costs can be reduced through further research and development. For example, not all the features of the Jetson Nano Developer Kit and Raspberry Pi were used. As such, an embedded device to replace both the Jetson Nano and Raspberry Pi could be developed to be tailored specifically for the needs of Waldo. This would in turn cut costs on the power supply used, since there would not be a need for such a large power bank to power both the Jetson Nano and the Raspberry Pi. In other words, a specifically customised rechargeable battery could be used instead, which would save on costs and space.

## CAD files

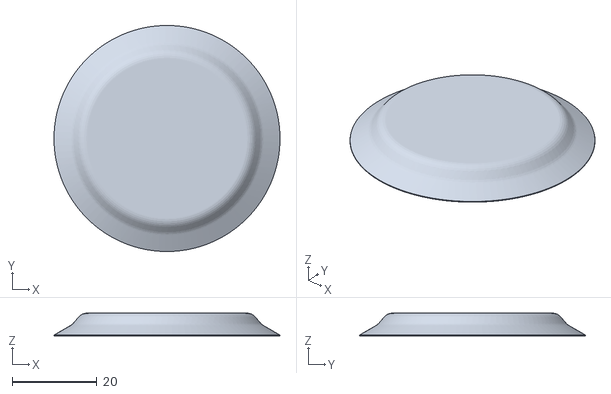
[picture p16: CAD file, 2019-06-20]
4-Hardware/4-1-3D-Printing-STL-Files/button support.stl
53.4 x 53.4 x 5.41

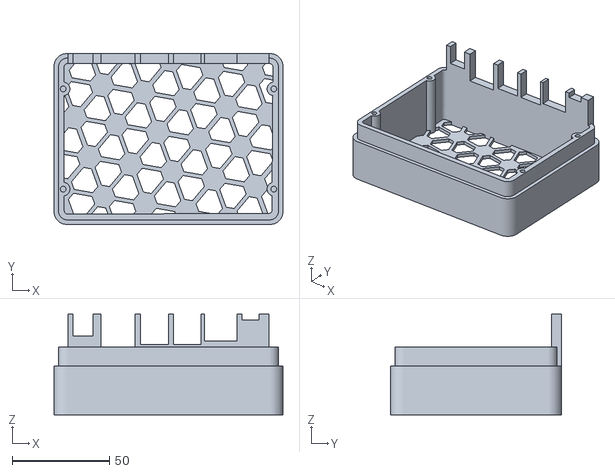
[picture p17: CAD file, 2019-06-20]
4-Hardware/4-1-3D-Printing-STL-Files/Jetson Nano Case/Top-Jetson-Nano-Case.stl
118.0 x 88.0 x 51.8

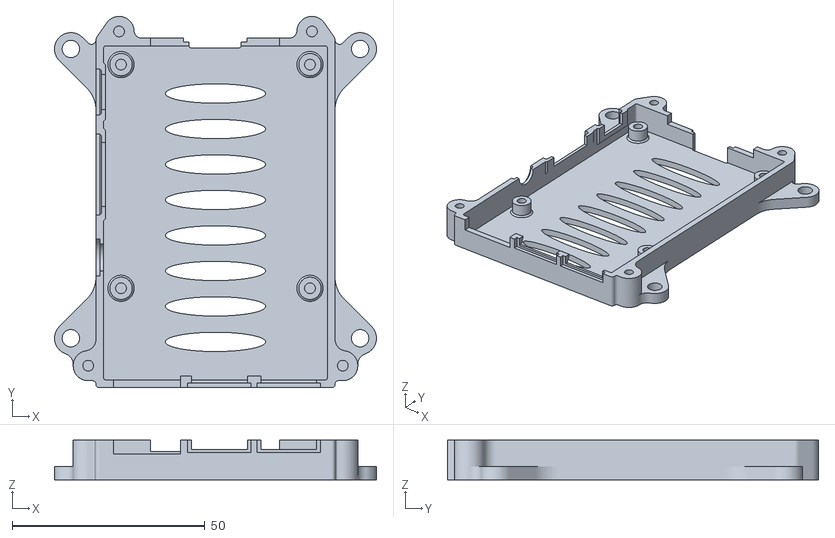
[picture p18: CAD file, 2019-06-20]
4-Hardware/4-1-3D-Printing-STL-Files/Raspberry Pi Case/rpi3-bottom.stl
83.5 x 96.2 x 10.3

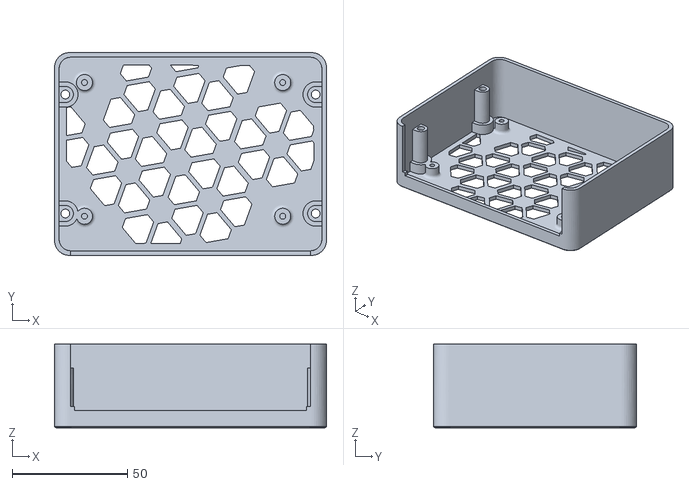
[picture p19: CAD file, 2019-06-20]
4-Hardware/4-1-3D-Printing-STL-Files/Jetson Nano Case/Bottom-Jetson-Nano-Case.stl
118.0 x 88.0 x 36.2

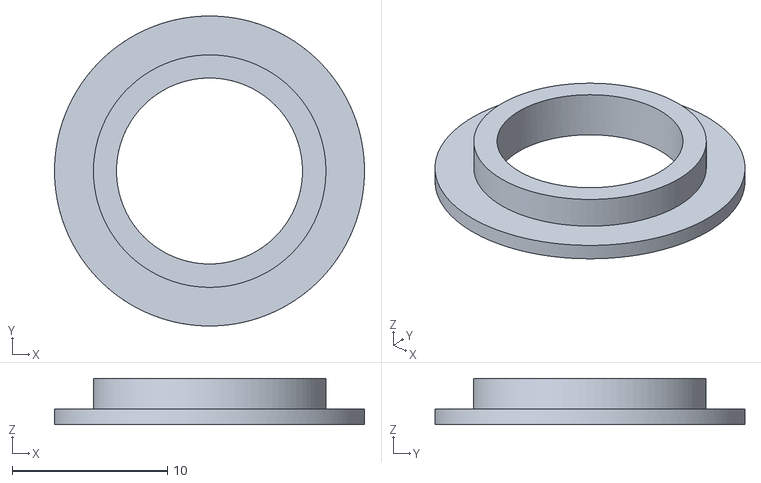
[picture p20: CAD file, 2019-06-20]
4-Hardware/4-1-3D-Printing-STL-Files/Waldo_eyepiece.stl
20.0 x 20.0 x 2.99

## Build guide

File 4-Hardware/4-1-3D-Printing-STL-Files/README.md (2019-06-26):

4.1 3D Printing STL Files
====================

This folder contains the STL files used for 3D printing components of WALDO. These components are:

* [Jetson Nano Case](https://github.com/patrickjohncyh/ibm-waldo/tree/master/4-Hardware/4-1-3D-Printing-STL-Files/Jetson%20Nano%20Case) (Obtained from: https://www.thingiverse.com/thing:3532828)
* [Raspberry Pi Case](https://github.com/patrickjohncyh/ibm-waldo/tree/master/4-Hardware/4-1-3D-Printing-STL-Files/Raspberry%20Pi%20Case) (Obtained from: https://www.thingiverse.com/thing:922740)
* [Eyepiece](https://github.com/patrickjohncyh/ibm-waldo/blob/master/4-Hardware/4-1-3D-Printing-STL-Files/Waldo_eyepiece.stl)
* [Button Support](https://github.com/patrickjohncyh/ibm-waldo/blob/master/4-Hardware/4-1-3D-Printing-STL-Files/button%20support.stl)

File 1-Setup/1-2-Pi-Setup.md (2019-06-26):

1.2 Raspberry Pi setup
===

This section provides a step-by-step guide on how to setup the Rasberry Pi 3 environment as used in WALDO.

## Go To
* 1.2.1 [Setting up a Raspberry Pi and OS](#121-setting-up-raspberry-pi-and-raspbian-os)
* 1.2.2 [Ensuring Pi is running an up to date OS version](#122-checking-pi-os-version)
* 1.2.3 [Installation of Packages](#123-installation-of-packages)
* 1.2.4 [GPIO Numbering Schemes](#124-gpio-numbering-schemes)

1.2.1 Setting up Raspberry Pi and Raspbian OS
---
1. A micro SD card is required to store Raspbian OS, and a power source of 5V and a minimum of 2.5A is [recommended](https://projects.raspberrypi.org/en/projects/raspberry-pi-setting-up/2) to power the Raspberry Pi 3. 
2. If an SD with Raspbian OS has been provided with the Pi, skip to step 4. If not, continue to step 3.
3. The first step to downloading the OS would be to head to the Raspberry Pi Downloads page from this [link](https://www.raspberrypi.org/downloads/). This link contains the files to download the NOOBS files which would be flashed into the SD card. The guide to formatting and copying of files over to the SD card can be found [here](https://projects.raspberrypi.org/en/projects/raspberry-pi-setting-up/3). 
4. Insert the SD card into the underside of the Pi. Connect the mouse and keyboard to the USB ports on the Pi. Lastly connect the HDMI cable from the Pi to a computer display the video output. 
5. Internet connectivity can either be through an Ethernet cable or through WiFi.
6. Connect the power cable to the Pi. The video output would display a boot up screen.
7. Adjust the date and time settings and language option for the Pi.

1.2.2 Checking Pi OS Version
---

The OS of the Pi must be checked to ensure that it is compatible with the setup described. 

In the current implementation, the Pi runs on Raspbian 1.2. Do make sure that the OS on your Pi is at least 1.2 or newer. This can be checked by entering the following command on the Pi’s terminal: `cat /etc/os-release`. 

1.2.3 Installation of Packages
---

1) IBM Watson Text-to-Speech is used to generate the audio files corresponding to detected Makaton Action or preset phrase. The IBM Watson API for python3 is required for this.

To install, run the following command in Terminal,

```
$ sudo pip3 install ibm-watson
``` 

2) NumPy library is used to perform certain mathematical computations. 

To install, run the following command in Terminal,

```
$ sudo apt-get install python3-numpy
```
1.2.4 GPIO Numbering Schemes
---

The Broadcom GPIO Numbers scheme (BCM) is used in this implementation. This scheme would mean that the pins are identified by their GPIO numbers instead of the pin numbering on the board. For example, in [3-Pi/pi-execution/main.py](https://github.com/patrickjohncyh/ibm-waldo/blob/master/3-Pi/pi-execution/main.py), input 1 is written as 22, which corresponds to Pin 15 on the Pi, which is labelled as GPIO22 instead of Pin 22 on the Pi. 

The image below is provided for easy reference. It shows the numbering of pins, as well as the GPIO tagged to the pins on the board. As mentioned above, in the BCM scheme, the GPIO numbers are used instead of the actual pin numbering on the board labelled as 1-40. 

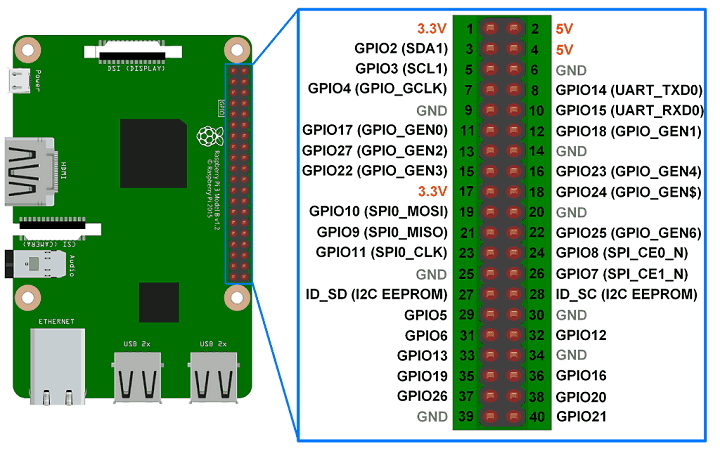
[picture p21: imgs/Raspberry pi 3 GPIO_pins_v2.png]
GPIO Pins


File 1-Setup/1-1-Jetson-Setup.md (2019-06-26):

1.1 Jetson Nano Setup
===
This section provides a step-by-step guide to successfully setup the environment for the Jetson Nano to perform Makaton sign recognition on a live video input from a webcam.

## Go To
* 1.1.1 [Operating System Setup](#111-operating-system-setup)
* 1.1.2 [Network Connectivity Setup](#112-network-connectivity-setup)
* 1.1.3 [Fan Cooling Setup](#113-fan-cooling-setup)
* 1.1.4 [Power Mode Selection](#114-power-mode-selection)
* 1.1.5 [Tensorflow Installation](#115-tensorflow-installation)
* 1.1.6 [OpenCV Installation](#116-opencv-installation)
* 1.1.7 [Jetson GPIO Installaton](#117-jetson-gpio-installation)
* 1.1.8 [GPU/CPU RAM Expansion using Swap File](#118-gpucpu-ram-expansion-using-swap-file)
* 1.1.9 [GPU Verification](#119-gpu-verification)
* 1.1.10 [Running the Model](#1110-running-the-model)

1.1.1 Operating System Setup
---

1. Prepare microSD card(Minimum requirement 16GB UHS-1 microSD) and plug-in power supply(20 W). A high speed microSD card is critical in the smooth running of the OS.
2. Download and flash with Jetson Nano Developer Kit SD Card Image on microSD Card following the instructions from this link : https://developer.nvidia.com/embedded/learn/get-started-jetson-nano-devkit#write
3. Place the Jetson Nano module on top of the paper stand provided and insert the microSD card (with system image already written to it) into the slot on the underside of the Jetson Nano module. 
4. Connect and power on computer display via HDMI to HDMI or HDMI to DVI. Connect a keyboard and a mouse to Jetson Nano and finally power on the Jetson Nano.
5. After completing the initial setup, log in and you should see this screen :

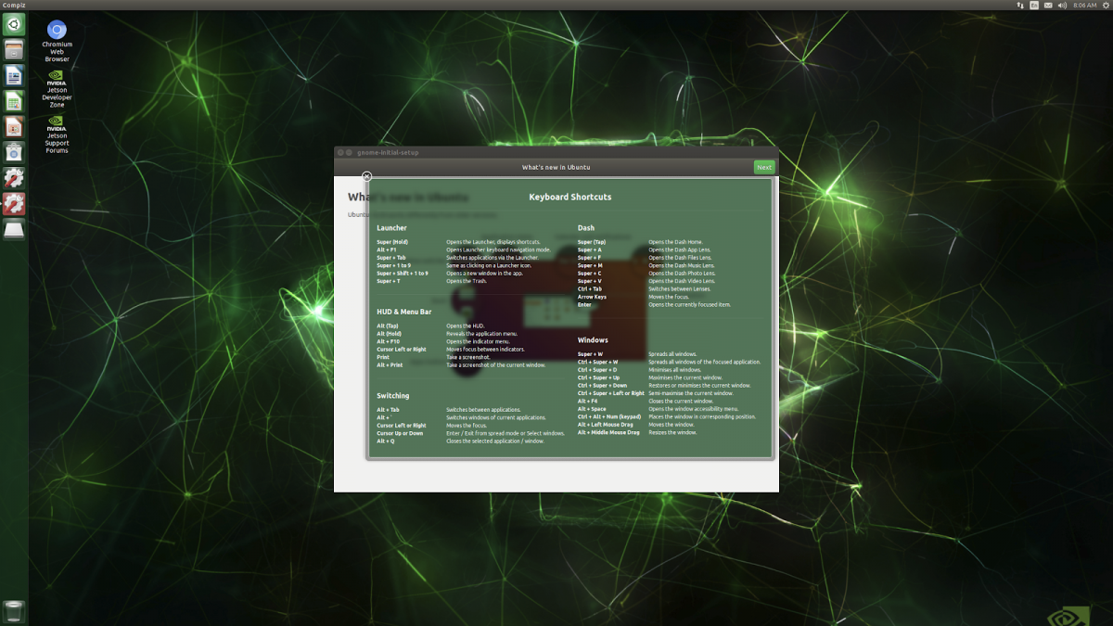
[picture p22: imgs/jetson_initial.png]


1.1.2 Network Connectivity Setup
---
1. Prepare Edimax EW-7811UN-N150 Wi-Fi USB Adaptor and an Ethernet cable.
2. Connect the Jetson Nano using the Ethernet cable.
3. Official built-in driver for EW-7811UN adaptor supports Linux kernel up to v3.9 only. For all other Linux kernels beyond v3.9, install the open source driver from github using a Command Line Interface(CLI) in a Terminal following the steps from this [link](https://askubuntu.com/questions/551522/netis-wf2120-wifi-adapter-drops-signal-within-seconds/551648#551648).
5. If Wi-Fi does not appear to connect, consider removing the Ethernet cable and trying again. During installation phase, it is advised to use Ethernet to ensure a consistent internet connection

1.1.3 Fan Cooling Setup
---
Adding a cooling fan will keep the Jetson from overheating and potentially stalling. To automatically initialise the cooling fan, a `cronjob` is added to call the `jetson_clocks` script at boot.
1. `$ sudo crontab -e`. You may be prompted for your password.
2. If this is your first time using a cronjob, select `nano` as your editor.
3. Add `@reboot /usr/bin/jetson_clocks` to the bottom of the file
4. `crtl-x` to exit, `Y` to confirm save and `Enter`
5. `$ sudo reboot`

1.1.4 Power Mode Selection
---
If facing power issues when running on a battery pack. The operating mode of the Jetson Nano can be altered to use less power.

1. To check the current operating model (default is Mode 0 NMAX)
```$ /usr/sbin/nvpmodel -q```

2. To set the model to Mode 1 5W,
```$ /usr/sbin/nvpmodel -m 1```
3. To make Mode 1 default,
	1. `$ sudo nano /etc/nvpmodel/nvpmodel_t210_jetson-nano.conf`
	2. At the bottom of the file, change `PM_CONFIG DEAFULT=N`, where N is the desired Mode (i.e 0 or 1)
4. It is possible to create a custom operating mode based on your requirements. For further information please refer to the official [documentation](https://docs.nvidia.com/jetson/l4t/index.html#page/Tegra%2520Linux%2520Driver%2520Package%2520Development%2520Guide%2Fpower_management_nano.html%23).
 
1.1.5 Tensorflow Installation
---
Adapted from https://docs.nvidia.com/deeplearning/frameworks/install-tf-jetson-platform/index.html

1. Update and upgrade apt-get:

```
$ sudo apt-get update
$ sudo apt-get upgrade
```

2. Install system packages as required by TensorFlow:

```
$ sudo apt-get install libhdf5-serial-dev hdf5-tools libhdf5-dev zlib1g-dev zip libjpeg8-dev
```

3. Install pip3

```
$ sudo apt-get install python3-pip
```

4. Install required python3 packaged for Tensorflow

```
$ sudo pip3 install -U numpy grpcio absl-py py-cpuinfo psutil portpicker six mock requests gast h5py astor termcolor protobuf keras-applications keras-preprocessing wrapt google-pasta tensorboard==1.13.0 tensorflow-estimator==1.13.0
```

5. Install the NVIDIA release of tensorflow-gpu for Jetson Nano

```
$ sudo pip3 install --extra-index-url https://developer.download.nvidia.com/compute/redist/jp/v42 tensorflow-gpu==$1.13.1+nv19.3
```

6. Verify that tensorflow-gpu is installed by importing into python3

```
$ python3
$ import tensorflow
```

1.1.6 OpenCV Installation
---

It is important to install OpenCV from source so as to reap the benefits of CUDA GPU acceleration.

1. On the Jetson Nano, navigate to the jetson-execution directory

2. Run the installation script for OpenCV

```
sudo ./install_opencv4.0.0_Nano.sh .
```

Script obtained from https://github.com/AastaNV/JEP/blob/master/script/install_opencv4.0.0_Nano.sh

1.1.7 Jetson GPIO Installation
---

Installing Jetson GPIO for python3.6 will enable control of the Jetson GPIO pins with python.

```
sudo pip3 install Jetson.GPIO
```

1.1.8 GPU/CPU RAM Expansion using Swap File
---
The Jetson Nano’s RAM is shared between the CPU and the GPU. To ensure that there is sufficient RAM for both, the Swap File is activated. This allows the SD card memory to be temporarily used as RAM.

To increase the amount of RAM available on Jetson Nano, (Only about \~2.7GB left after allocation to kernel) go to the following site and follow the instructions provided :
https://www.jetsonhacks.com/2019/04/14/jetson-nano-use-more-memory/

1.1.9 GPU Verification
---
Enter the 2-MachineLearning/jetson-execution folder,
Run `python3 sanity/tf-test.py` to verify that the Jetson Nano GPU is being utilised by tensorflow. The output should show that there is one GPU allocated.

1.1.10 Running the Model
---
In the 2-MachineLearning/jetson-execution folder,
start the demo by running the following command in terminal,

```
sudo python3 demo.py
```

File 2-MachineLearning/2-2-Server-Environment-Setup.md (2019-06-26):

2.2 Server Environment Setup
===

This section provides the basic instructions on how to setup a server to perform Machine Learning on Keras+Tensorflow. The [server-training folder](https://github.com/patrickjohncyh/ibm-waldo/tree/master/2-MachineLearning/server-training) provides the code to perform training on the 6 actions as detailed in [Section 2.1 - Machine Learning](https://github.com/patrickjohncyh/ibm-waldo/blob/master/2-MachineLearning/2-1-Machine-Learning.md).

## Go To
* 2.2.1 [Installing Nvidia Driver, CUDA and cuDNN](#221-installing-nvidia-driver-cuda-and-cudnn)
* 2.2.2 [Installing Python packages](#222-installing-python-packages)
* 2.2.3 [Download 20BN-Jester Dataset](#223-download-20bn-jester-dataset)
* 2.2.4 [Generate training CSV](#224-generate-training-csv)
* 2.2.5 [Training](#225-training)

2.2.1 Installing Nvidia Driver, CUDA and cuDNN
---

You may refer to this [link](https://medium.com/@zhanwenchen/install-cuda-and-cudnn-for-tensorflow-gpu-on-ubuntu-79306e4ac04e) for step-by-step instructions on installing and setting up your Nvidia driver, CUDA and cuDNN to exploit GPU capabilities for machine learning training.

Note : Versions listed on that site may be outdated, but you can check their compatibility via these sites - [Nvidia Driver and CUDA compatibility](https://stackoverflow.com/questions/30820513/what-is-the-correct-version-of-cuda-for-my-nvidia-driver/30820690#30820690) and [CUDA and cuDNN compatibility](https://docs.nvidia.com/deeplearning/sdk/cudnn-support-matrix/index.html)

The steps from the link above may be summarised as follows:

1. Install Nvidia Driver on your machine via `sudo apt-get install nvidia-410 nvidia-modprobe` (We used V410.48, you can enter `nvidia-smi` on terminal to check your existing Nvidia Driver version if you already have one).

2. Download and Install a version of CUDA that is compatible with your Nvidia driver (We used CUDA V10.0 and enter `nvcc --version` to check if you already have CUDA).

3. Download and Install a version of cuDNN that is compatible with the CUDA version you installed. (We used CUDNN 7.5.0 and you may enter `CUDNN_H_PATH=$(whereis cudnn.h)` followed by `cat ${CUDNN_H_PATH} | grep CUDNN_MAJOR -A 2` to check your cuDNN version if you already have cuDNN installed.

2.2.2 Installing Python packages
---

We used Python v3.5.2 but we recommend v3.6.8 or the latest version for compatibility with performing inference on Jetson Nano.

1.  Ensure python3 version is up to date and at least 3.6.8 (run `python3 -v` to verify)
 
2.  Get pip3 by entering `sudo apt-get install python3-pip`

3.  From the MachineLearning folder directory, run the following command to install the required python3 packages on to the server/machine for further training : `pip3 install -r requirements.txt`

Below is a summary of the main packages required and the versions we used for model training:

h5py==2.9.0

imageio==2.5.0

imgaug==0.2.9

Keras==2.2.4

Keras-Applications==1.0.7

Keras-Preprocessing==1.0.9

matplotlib==3.0.3

numpy==1.16.4

pandas==0.24.2

Pillow==6.0.0

scikit-image==0.15.0

scikit-learn==0.20.3

scipy==1.3.0

tensorflow==1.13.1

tensorflow-gpu==1.13.1

tqdm==4.31.1

2.2.3 Download 20BN-Jester Dataset
---

You may obtain and download the Jester Dataset from [here](https://20bn.com/datasets/jester)

2.2.4 Generate training CSV
---

To generate the CSV used for training, run `python3 utils/gen-training-csv.py`.
You may also select the actions for the model to train on by editing the mask in the python file.

2.2.5 Training
---

To begin training the model, run `python3 training.py`

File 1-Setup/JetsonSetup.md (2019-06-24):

1.1 Jetson Nano Setup
===
This section details a step-by-step guide to successfully setup the environment for the Jetson Nano to perform Makaton sign recognition on a live video input from a webcam.

1.1.1 Operating System Setup
---

1. Prepare microSD card(Minimum requirement 16GB UHS-1 microSD) and plug-in power supply(20 W). A high speed microSD card is critical in the smooth running of the OS.
2. Download and flash with Jetson Nano Developer Kit SD Card Image on microSD Card following the instructions from this link : https://developer.nvidia.com/embedded/learn/get-started-jetson-nano-devkit#write
3. Place the Jetson Nano module on top of the paper stand provided and insert the microSD card (with system image already written to it) into the slot on the underside of the Jetson Nano module. 
4. Connect and power on computer display via HDMI to HDMI or HDMI to DVI. Connect a keyboard and a mouse to Jetson Nano and finally power on the Jetson Nano.
5. After completing the initial setup, log in and you should see this screen :



1.1.2 Network Connectivity Setup
---
1. Prepare Edimax EW-7811UN-N150 Wi-Fi USB Adaptor and an Ethernet cable.
2. Connect the Jetson Nano using the Ethernet cable.
3. Official built-in driver for EW-7811UN adaptor supports Linux kernel up to v3.9 only. For all other Linux kernels beyond v3.9, install the open source driver from github using a Command Line Interface(CLI) in a Terminal following the steps from this [link](https://askubuntu.com/questions/551522/netis-wf2120-wifi-adapter-drops-signal-within-seconds/551648#551648).
5. If Wi-Fi does not appear to connect, consider removing the Ethernet cable and trying again. During installation phase, it is advised to use Ethernet to ensure a consistent internet connection

1.1.3 Fan Cooling Setup
---
Adding a cooling fan will keep the Jetson from overheating and potentially stalling. To automatically initialise the cooling fan, a `cronjob` is added to call the `jetson_clocks` script at boot.
1. `$ sudo crontab -e`. You may be prompted for your password.
2. If this is your first time using a cronjob, select `nano` as your editor.
3. Add `@reboot /usr/bin/jetson_clocks` to the bottom of the file
4. `crtl-x` to exit, `Y` to confirm save and `Enter`
5. `$ sudo reboot`

1.1.4 Power Mode Selection
---
If facing power issues when running on a battery pack. The operating mode of the Jetson Nano can be altered to use less power.

1. To check the current operating model (default is Mode 0 NMAX)
```$ /usr/sbin/nvpmodel -q```

2. To set the model to Mode 1 5W,
```$ /usr/sbin/nvpmodel -m 1```
3. To make Mode 1 default,
	1. `$ sudo nano /etc/nvpmodel/nvpmodel_t210_jetson-nano.conf`
	2. At the bottom of the file, change ‘PM_CONFIG DEAFULT=N’, where N is the desired Mode (i.e 0 or 1)
4. It is possible to create a custom operating mode based on your requirements. For further information please refer to the official [documentation](https://docs.nvidia.com/jetson/l4t/index.html#page/Tegra%2520Linux%2520Driver%2520Package%2520Development%2520Guide%2Fpower_management_nano.html%23).
 
1.1.5 Tensorflow Installation
---
Adapted from https://docs.nvidia.com/deeplearning/frameworks/install-tf-jetson-platform/index.html

1. Update and upgrade apt-get:

```
$ sudo apt-get update
$ sudo apt-get upgrade
```

2. Install system packages as required by TensorFlow:

```
$ sudo apt-get install libhdf5-serial-dev hdf5-tools libhdf5-dev zlib1g-dev zip libjpeg8-dev
```

3. Install pip3

```
$ sudo apt-get install python3-pip
```

4. Install required python3 packaged for Tensorflow

```
$ sudo pip3 install -U numpy grpcio absl-py py-cpuinfo psutil portpicker six mock requests gast h5py astor termcolor protobuf keras-applications keras-preprocessing wrapt google-pasta tensorboard==1.13.0 tensorflow-estimator==1.13.0
```

5. Install the NVIDIA release of tensorflow-gpu for Jetson Nano

```
$ sudo pip3 install --extra-index-url https://developer.download.nvidia.com/compute/redist/jp/v42 tensorflow-gpu==$1.13.1+nv NEED CHECK
```

6. Verify that tensorflow-gpu is installed by importing into python3

```
$ python3
$ import tensorflow
```

1.1.6 OpenCV Installation
---

It is important to install OpenCV from source so as to reap the benefits of CUDA GPU acceleration.

1. Navigate to the waldo directory

2. Run the installation script for OpenCV

```
sudo ./install_opencv4.0.0_Nano.sh .
```

Script obtained from https://github.com/AastaNV/JEP/blob/master/script/install_opencv4.0.0_Nano.sh

1.1.7 Jetson GPIO Installaton
---

Installing Jetson GPIO for python3.6 will enable control of the Jetson GPIO pins with python.

```
sudo pip3 install  PUT ACTUAL PACAKGE HERE
```

1.1.8 GPU/CPU RAM Expansion using Swap File
---
The Jetson Nano’s RAM is shared between the CPU and the GPU. To ensure that there is sufficient RAM for both, the Swap File is activated. This allows the SD card memory to be temporarily used as RAM.

To increase the amount of RAM available on Jetson Nano, (Only about \~2.7GB left after allocation to kernel) go to the following site and follow the instructions provided :
https://www.jetsonhacks.com/2019/04/14/jetson-nano-use-more-memory/

1.1.9 GPU Verification
---
Enter the 2-MachineLearning/jetson-execution folder,
Run `python3 sanity/tf-test.py` to verify that the Jetson Nano GPU is being utilised by tensorflow.

1.1.10 Running the Model
---
In the 2-MachineLearning/jetson-execution folder,
start the demo by running the following command in terminal,`python3 demo.py`

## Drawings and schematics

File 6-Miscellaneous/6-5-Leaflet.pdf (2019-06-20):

# Hardware and Capabilities Team

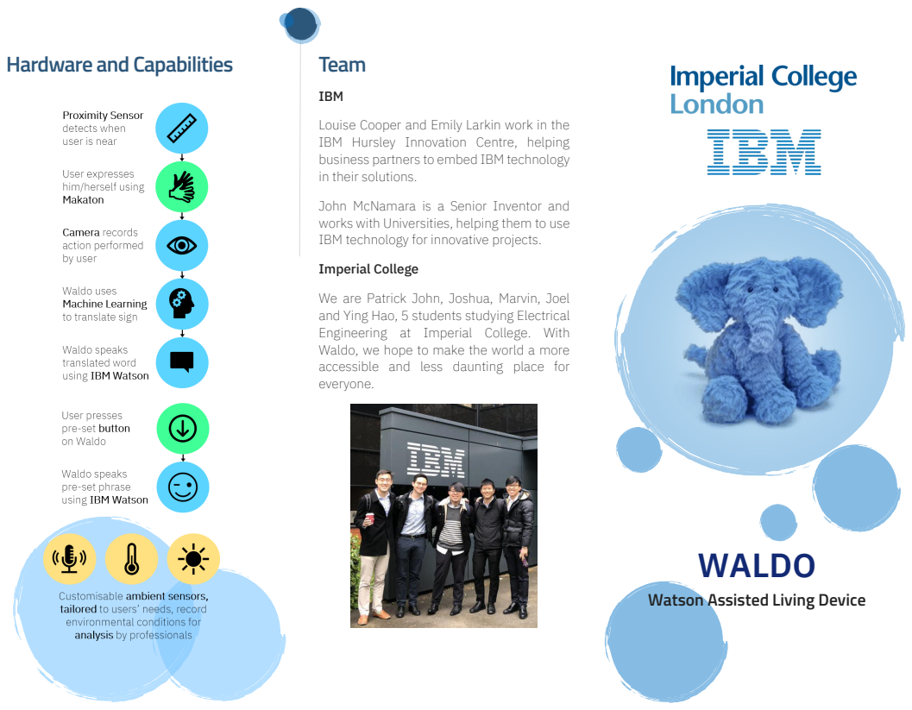
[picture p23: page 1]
IBM; Imperial College

Louise Cooper and Emily Larkin work in the
IBM Hursley Innovation Centre, helping
business partners to embed IBM technology
in their solutions.

John McNamara is a Senior Inventor and
works with Universities, helping them to use
IBM technology for innovative projects.

We are Patrick John, Joshua, Marvin, Joel
and Ying Hao, 5 students studying Electrical
Engineering at Imperial College. With
Waldo, we hope to make the world a more
accessible and less daunting place for
everyone.

WALDO
Watson Assisted Living Device

# Makaton

Communication is one of the cornerstones of daily life, yet every day, many children and adults struggle to effectively express themselves.

What is Makaton?

Makaton is a language programme that uses signs and symbols to help people who have no speech or whose speech is unclear to communicate. Makaton is very flexible, and can be personalised to a level suitable to the individual. Today, over 100,000 children and adults use Makaton.

# Waldo

Waldo is a:

- Cute, endearing device that children and adults alike would be happy to use
- | Capable, | low | latency | Makaton
interpreter to augment the capabilities
| of carers
- Everyday companion device that helps users to quickly and effectively express
| themselves

# Market Potential

The market for adult specialist care in the UK is large, yet faces staffing problems such as high turnover and staff shortages.

Waldo fills a gap in the adult specialist care market by providing an affordable device that allows carers to understand Makaton without time-consuming study.

# Machine Learning

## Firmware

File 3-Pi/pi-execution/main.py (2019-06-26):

import RPi.GPIO as GPIO
import time
import os
import math
import numpy
from collections import deque
import sys

input1 = 22 
input2 = 27
input3 = 17
input4 = 5

input_us = 14

makin3 = 9  #lsb
makin2 = 11
makin1 = 10 #msb

def playSound(fileNum):
        os.system('aplay ' + 'audio_files/'+str(fileNum)+ '.wav')

def main():
    print('Script Running')
    sys.stdout.flush()
    GPIO.setmode(GPIO.BCM) #BCM pin numbering scheme from Pi
    
    GPIO.setup(input1, GPIO.IN)
    GPIO.setup(input2, GPIO.IN)
    GPIO.setup(input3, GPIO.IN)
    GPIO.setup(input4, GPIO.IN)

    GPIO.setup(makin1, GPIO.IN, pull_up_down=GPIO.PUD_DOWN)
    GPIO.setup(makin2, GPIO.IN, pull_up_down=GPIO.PUD_DOWN)
    GPIO.setup(makin3, GPIO.IN, pull_up_down=GPIO.PUD_DOWN)

    distarray = deque(maxlen=5)                
    mak1 = 0
    mak2 = 0
    mak3 = 0
    #while((mak1,mak2,mak3)!=(1,1,1)):
    while(0):
        mak1 = GPIO.input(makin1)
        mak2 = GPIO.input(makin2)
        mak3 = GPIO.input(makin3)
        #print((mak1,mak2,mak3))
        time.sleep(0.1)

    playSound(7)
    print('Jetson Initialised')
    sys.stdout.flush()

    while True:

        # Read Inputs
        value1 = GPIO.input(input1)
        value2 = GPIO.input(input2)
        value3 = GPIO.input(input3)
        value4 = GPIO.input(input4)
        mak1 = GPIO.input(makin1)
        mak2 = GPIO.input(makin2)
        mak3 = GPIO.input(makin3)

        # Read Ultrasonic
        GPIO.setup (input_us, GPIO.OUT)
        GPIO.output(input_us, False)
        GPIO.output(input_us, True )
        GPIO.output(input_us, False)
        GPIO.setup(input_us,GPIO.IN)

        while GPIO.input(14) == 0:
            start_time = time.time()

        while GPIO.input(14) == 1:
            end_time = time.time()
            duration = end_time - start_time
            distance = duration * 34000 / 2
            distarray.append(math.floor(distance))
        
        # Use Median of Last 5 Readings
        finalDist = numpy.median(distarray)
                
        if finalDist < 5:
            time.sleep(0.1)
        else:
            if value1:
                playSound(0)
            elif value2:
                playSound(1)
            elif value3:
                playSound(2)
            elif value4:
                playSound(3)

            if(finalDist>=55 and finalDist<70):                
                playSound(5)

            if(finalDist>=70):
                if((mak1,mak2,mak3) == (0,0,1)):
                    playSound('Dinner')
                elif((mak1,mak2,mak3) == (0,1,0)):
                    playSound('Good')
                elif((mak1,mak2,mak3) == (0,1,1)):
                    playSound('Home')
                elif((mak1,mak2,mak3) == (1,0,0)):
                    playSound('No')
                elif((mak1,mak2,mak3) == (1,0,1)):
                    playSound('Sorry')
            time.sleep(0.25)

if __name__ == '__main__':
    main()

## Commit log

2019-05-09 Decent Implementation with CNN +LSTM
    [jester-v1-train-five.csv]
2019-05-09 Removed duplicate folder
    [jester-v1-train-five.csv]
2019-05-13 Complete first implementation using CNN LSTM method
    [jester-v2-train-five.csv, jester-v3-train-five.csv]
2019-05-15 Clean up and improved model by adding Norm layer
    [jester-v4-train-five.csv]
2019-05-15 Clean up code before further progress
    [jester-train.csv, jester-v1-train-five.csv, jester-v2-train-five.csv, jester-v3-train-five.csv]
2019-05-16 Add training log for C3D + LSTM. C3D used pretrained weights on Sports1M dataset with the later conv layers unfrozen. Number of frames also increased from 16 to 30.
2019-05-16 Text to speech module implemented on python
    [jester-train.csv]
2019-05-20 Unfreeze more layers on C3D+LSTM which attained better performance. Implement IBM watson text to speech. Begin work on conversion of model to run on jetson
    [jester-train-12.csv]
2019-05-21 Investigated Feature Embeddings of C3D+LSTM Model and started implementing Model on our own collected dataset
    [jester-train-12.csv, vids_csv.csv]
2019-05-27 Add code to test inference speed. Add minimized model c3d_lite and c3d_super_lite (~8 fps on jetson).
    [vids_csv.csv]
2019-05-28 Fix csv error due to merge
    [vids_csv.csv]
2019-06-19 Update Power Source.md
2019-06-21 Create Raspberry Pi Case
2019-06-21 Rename stl files
    [Jetson-Nano-Case.stl, Top-Jetson-Nano-Case.stl, rpi3-bottom.stl]
2019-06-21 Remove legacy code
    [jester-train-12.csv, jester-train.csv, vids_csv.csv]
2019-06-21 Add training code that runs on server
    [jester-train-all.csv]
2019-06-21 Update ML docuemntation with further details. Update training code to train on 6 actions as per docuemntation.
    [jester-train-six-actions.csv]
2019-06-24 Update and rename Bill_of_Materials.md to 5-3-Bill-of-Materials.md
2019-06-24 rename hardware files
    [Bottom-Jetson-Nano-Case.stl, Top-Jetson-Nano-Case.stl, Waldo_eyepiece.stl, button support.stl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]
2019-06-24 Update and rename 4-3-Power-Source.md to 4-2-Power-Supply.md
2019-06-24 Remove bracket
